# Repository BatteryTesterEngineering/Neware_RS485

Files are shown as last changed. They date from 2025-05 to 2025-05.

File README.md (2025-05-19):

# Neware BTS4000 RS-485 Protocol
This work is the reverse engineering of the Neware BTS4000 series battery cyclers RS-485 communication protocol.

## Division of Responsibilities
The Middle Machine is responsible for control and intepretation of the vast majority of the battery testing process, while the battery cyclers exclusively respond to commands from the middle machine.

For example, the termination conditions for test steps are evaluated and handled by the middle machine. The cyclers report current and voltage values as ADC readings, which the middle machine then converts to physical values. The testers themselves do run the active feedback control to maintain specified physical conditions: current, power, voltage, etc.

| Middle Machine   | Tester         | 
| --------- | ------------- | 
| Evaluates step termination conditions | Active feedback control to maintain step conditions (IE constant current, constant power, etc.) |
| Converts ADC values to physical values |  Sets channel LED status based on channel activity       | 
| Sets the data aquisition frequency    | Continuously Samples the ADCs  |

## RS-485 Bus
The Neware BTS4000 battery cycler system uses a full-duplex, 3 Mbps RS-485 physical bus to connect the middle machine to all of the test units.

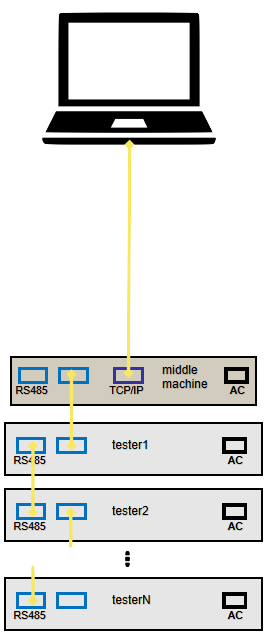
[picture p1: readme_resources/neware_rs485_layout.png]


RS-485 layout from [Neware's official guide](https://newarebattery.com/how-to-start-to-use-neware-bst4000-series/)

### Bus UART Settings

| Setting   | Value         | 
| --------- | ------------- | 
| Baud Rate | 3,000,000 bps | 
| Byte Size | 8 bits        | 
| Parity    | None          | 
| Stop Bits | 1             | 

### Full-Duplex
The RS-485 implementation by Neware is ***full-duplex***. Note that this is relatively unusual for RS-485 implementations. That means that the controller (middle machine) transmits messages on one channel (twisted copper pair), and the receivers (testers) transmit on another channel. 

> Side note: This could have been implemented as a half-duplex bus. This full-duplex communication is not technically needed, as the middle machine must send a request before any tester responds and the testers only respond after the middle machine requests. However, if the two channels are bridged, the communications fail between the middle machine and the testers. So, I guess, full-duplex it is.

### Pinout
The Neware BTS4000 middle machine and testers use RJ45 jacks and standard ethernet cables for RS-485 communications. Each machine has two ports which are wired in electrical parallel to allow for easy daisy chaining. There is no difference between the two ports.

The pinout is as follows:

| Middle Machine Function  | Tester Function | Ethernet Wire Color (T568B) | RJ45 Pin |
| ------ | ------ | ------------ | - |
| R- (B) | T- (Z) | Green        | 6 |
| R+ (A) | T+ (Y) | Green/White  | 3 |
| T- (Z) | R- (B) | Orange       | 2 |
| T+ (Y) | R+ (A) | Orange/White | 1 |
| GND    | GND    | Brown        | 8 |
| GND    | GND    | Brown/White  | 7 |

> RJ45 pins 4 and 5 (Ethernet T568B colors Blue and Blue/White) are unused.

## Neware Communication Protocol
The protocol appears to be a custom implementation on top of RS-485 and does not follow common standards such as Modbus RTU, Profibus, DMX512, BACnet MS/TP, etc.

### Overview
The middle machine begins all communications. Every response from the testers is a direct response to a request from the middle machine. The testers have a watchdog timeout such that they will turn off all charge or discharge activity on all channels if they do not hear a message from the middle machine every few seconds.

Every message is 36 bytes long and consists of one byte of machine addressing, one byte of channel addressing, one byte of message type ID, a one byte CRC, and 32 bytes of payload.

| byte 0 | byte 1 | byte 2 | byte 3 | bytes 4 - 35 |
| ------ | ------ | ------ | ------ | ------------ |
| Machine ID | Channel ID | Message Type ID | CRC | Message Type Dependent Payload

> Note: There is no time information provided by the testers. All timestamps are added upon message reception by the middle machine.

### Machine Addressing
Machine ID is 0 indexed, while it is presented to the user as 1 indexed. IE Machine ID 0 corresponds to the tester with ID 1.

### Channel Addressing
Channel ID is 0 indexed, while it is presented to the user as 1 indexed. IE Channel ID 7 corresponds to the tester Channel 8.

### Message Type ID
The message type ID byte defines what the message type is. Specifically, bit 0 is flag for request ('0' if the message is a request/comes from the middle machine) or response ('1' if the message is a response/comes from a tester), and the remaining seven bits define the message type.

| bit 0 | bits 1-7 |
| ----- | -------- |
| Request (0) / Response (1) Flag | Message Type |

Some known message type IDs are defined below:

| ID | Description |
| ----- | -------- |
| 0x00  | Tester Response (Ping) Request |
| 0x80  | Tester Presence (Ping) Acknowledge |
| 0x02  | Change Unit ID Request |
| 0x82  | Change Unit ID Acknowledge |
| 0x17  | Constant Voltage Charge Request |
| 0x97  | Constant Voltage Charge Acknowledge |
| 0x18  | Constant Voltage Discharge Request |
| 0x98  | Constant Voltage Discharge Acknowledge |
| 0x1A  | Constant Current Charge Request |
| 0x9A  | Constant Current Charge Acknowledge |
| 0x1B  | Constant Current Discharge Request |
| 0x9B  | Constant Current Discharge Acknowledge |
| 0x1C  | Constant Power Discharge Request |
| 0x9C  | Constant Power Discharge Acknowledge |
| 0x1F  | Voltage and Current Request |
| 0x9F  | Voltage and Current Acknowledge |
| 0x25  | End of Test Request |
| 0xA5  | End of Test Acknowledge |
| 0x31  | Constant Power Charge Request |
| 0xB1  | Constant Power Charge Acknowledge |

### CRC
The CRC byte is a crc8-maxim-dow calculated on a modified message. Since the CRC byte is in the middle of the message instead of at the end, the process of using it is a bit unusual. The CRC is calculated on the full 36 byte message, with a dummy 0x00 value subbed into byte 3. The calculated CRC is then swapped into byte 3 before the message is transmitted.

**Transmission CRC Calculation**:
1. Build the message as intended, leave a dummy '0x00' value in byte 3.
2. Calculate the CRC using a crc8-maxim-dow algorithm on the 36 byte message with the dummy byte.
3. Place the calculated CRC in byte 3.
4. Transmit the 36 byte message.

**Reception CRC Checking**:
1. Receive the 36 byte message.
2. Copy the CRC out of byte 3.
3. Replace byte 3 with '0x00'
4. Calculate the CRC using a crc8-maxim-dow algorithm on the 36 byte message with the dummy byte
5. Compare the calculated CRC with the stored CRC from the message, checking for equality

-- Or --

4. Append the copied CRC byte to the end of the message
5. Calculate the CRC using a crc8-maxim-dow algorithm on the now 37 byte array (message + appended CRC)
6. Check the calculated CRC for equality with '0x00'

### Payload
The payload is message type dependent. Some known payloads are described below.

**Message 0x17: Constant Voltage Charge Request**

| Name | Byte Position | Physical Value to Bus Value Mapping |
| ----- | -------- | ----- |
| Voltage  | Bytes 4-7 | Physical Value = Bus Value / 3225.6 |

**Message 0x97: Constant Voltage Charge Acknowledge**

There is no payload for a Constant Voltage Charge Acknowledge

**Message 0x1A: Constant Current Charge Request**

| Name | Byte Position | Physical Value to Bus Value Mapping |
| ----- | -------- | ----- |
| Current  | Bytes 4-7 | Physical Value = Bus Value / Current Range Divisor |
| Current Range  | Byte 8 | See Table in 0x9F: Voltage and Current Acknowledge |

**Message 0x9A: Constant Current Charge Acknowledge**

There is no payload for a Constant Current Charge Acknowledge

**Message 0x1B: Constant Current Discharge Request**

| Name | Byte Position | Physical Value to Bus Value Mapping |
| ----- | -------- | ----- |
| Current  | Bytes 4-7 | Physical Value = Bus Value / Current Range Divisor |
| Current Range  | Byte 8 | See Table in 0x9F: Voltage and Current Acknowledge |

**Message 0x9B: Constant Current Discharge Acknowledge**

There is no payload for a Constant Current Discharge Acknowledge

**Message 0x1C: Constant Power Discharge Request**

| Name | Byte Position | Physical Value to Bus Value Mapping |
| ----- | -------- | ----- |
| Power  | Bytes 4-7 | Physical Value = Bus Value / Power Range Divisor |
| Power Range  | Byte 12 | See Table |

Strangely, only power range of 0x02 has ever been seen in logs, when setting the power value from 0.5W to 60W

| Power Range | Name | Description | Power Range Divisor |
| ----- | -------- | ----- | -------- |
| 0x00  | Low Range | ? A | ? |
| 0x01  | Mid Range | ? A | ? |
| 0x02  | High Range | 0 - 60 W | 268.8 |

**Message 0x9C: Constant Power Discharge Acknowledge**

There is no payload for a Constant Power Discharge Acknowledge

**Message 0x1F: Voltage and Current Request**

There is no payload for a Voltage and Current Request

**Message 0x9F: Voltage and Current Acknowledge**

| Name | Byte Position | Physical Value to Bus Value Mapping |
| ----- | -------- | ----- |
| Voltage  | Bytes 4-7 | Physical Value = Bus Value / 3225.6 |
| Current  | Bytes 8-11 | Physical Value = Bus Value / Current Range Divisor |
| Current Range  | Byte 33 | See Table |
| Channel Status | Byte 35 | See Table |

| Current Range | Name | Description | Current Range Divisor |
| ----- | -------- | ----- | -------- |
| 0x00  | Low Range | 0 - 1 A | 16128 |
| 0x01  | Mid Range | 1 - 6 A | 2688 |
| 0x02  | High Range | 6 - 12 A | 1344 |

| Channel Status | Description |
| ----- | ----- |
| 0x00  | Channel Active |
| 0x01  | Channel Invalid/Error |
| 0x02  | Channel Rest |

**Message 0x25: End of Test Request**

There is no payload for an End of Test Request

**Message 0xA5: End of Test Acknowledge**

There is no payload for an End of Test Acknowledge

**Message 0x31: Constant Power Charge Request**

| Name | Byte Position | Physical Value to Bus Value Mapping |
| ----- | -------- | ----- |
| Power  | Bytes 4-7 | Physical Value = Bus Value / Power Range Divisor |
| Power Range  | Byte 12 | See Table |

Strangely, only power range of 0x02 has ever been seen in logs, when setting the power value from 0.5W to 60W

| Power Range | Name | Description | Power Range Divisor |
| ----- | -------- | ----- | -------- |
| 0x00  | Low Range | ? A | ? |
| 0x01  | Mid Range | ? A | ? |
| 0x02  | High Range | 0 - 60 W | 268.8 |

**Message 0xB1: Constant Power Charge Acknowledge**

There is no payload for a Constant Power Charge Acknowledge

***TODO! Add more***

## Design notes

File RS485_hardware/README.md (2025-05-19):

# Neware BTS4000 RS485 USB Interface

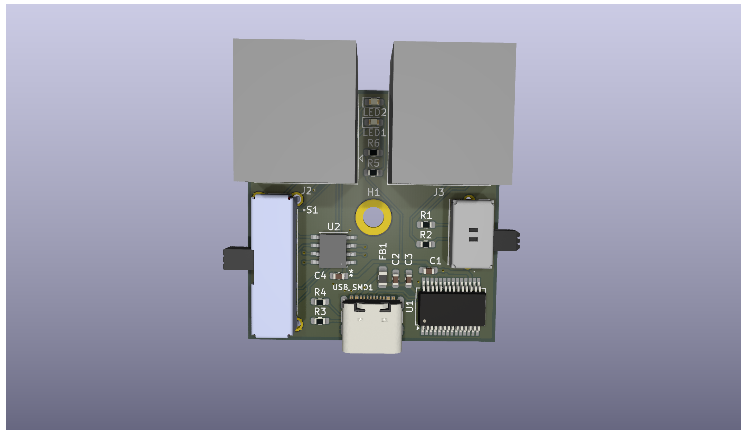
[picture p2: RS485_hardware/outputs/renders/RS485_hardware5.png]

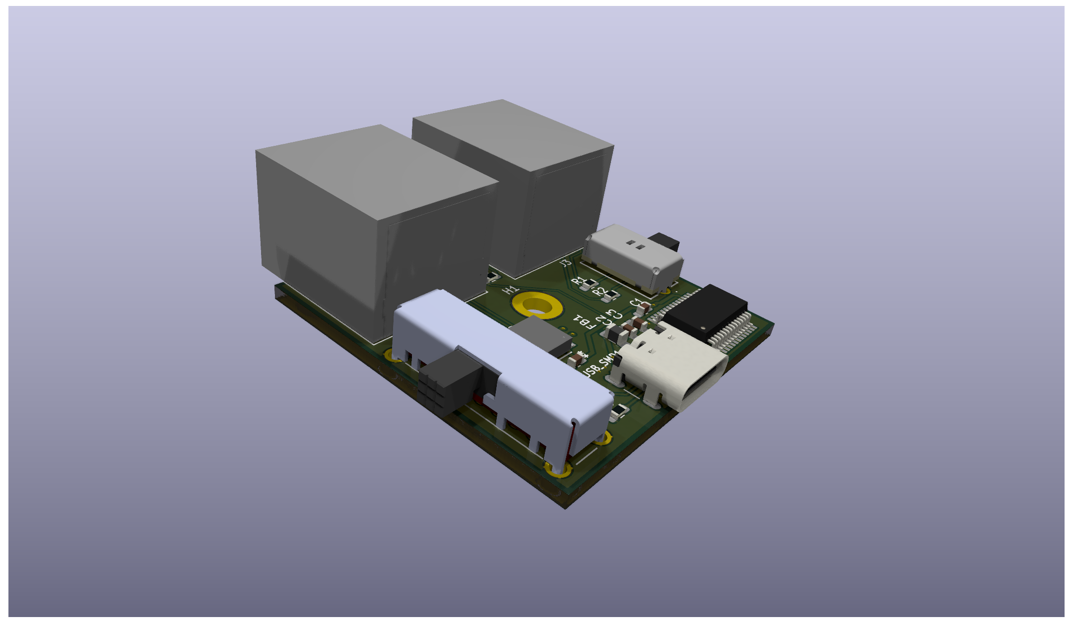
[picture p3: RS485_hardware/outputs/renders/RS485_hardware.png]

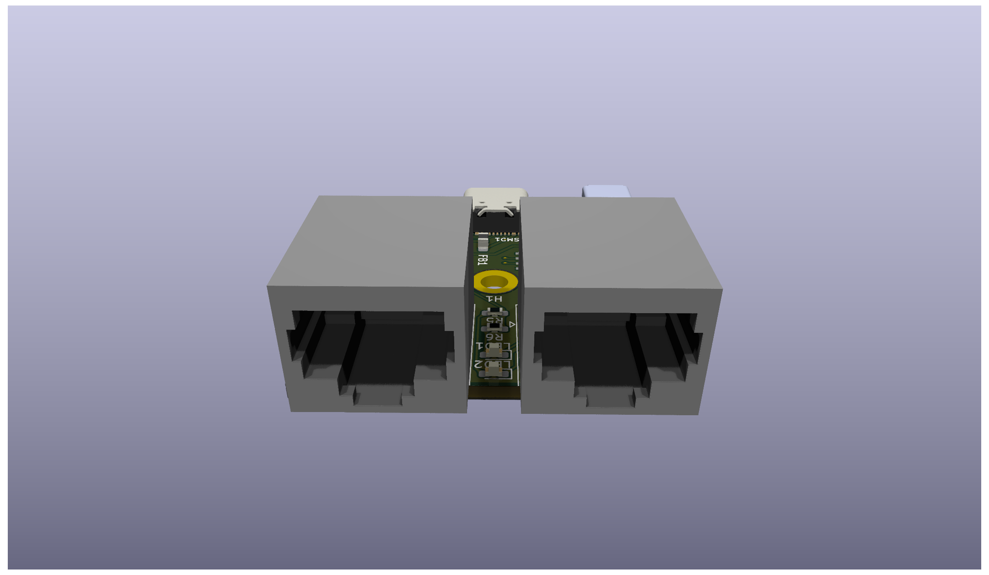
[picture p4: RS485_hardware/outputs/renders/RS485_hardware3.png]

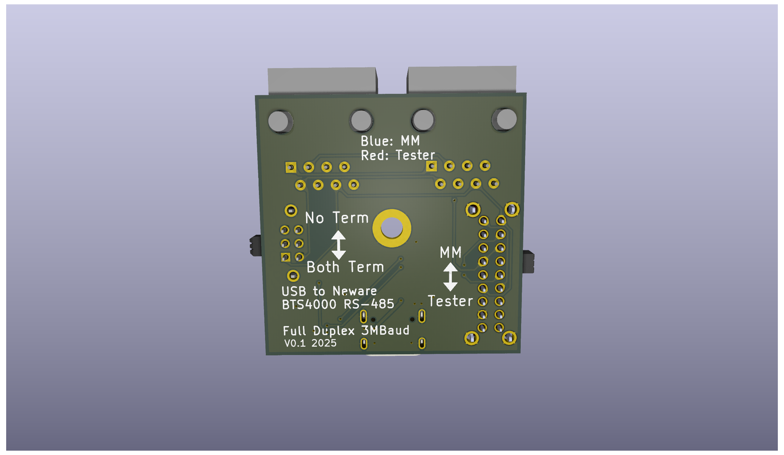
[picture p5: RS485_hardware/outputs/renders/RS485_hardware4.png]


This is the Kicad project and output files for a USB Adapter that allows any computer to listen and transmit on the Neware BTS4000 RS485 bus. The adapter is based on the FTDI FT232RN chip, which includes drivers for all major operating systems. The transciever is a MaxLinear SP3077E, which allows for full duplex 3MBaud communication.

## RS485 Bus Connectors
The bus connectors are intended to duplicate the RS485 bus connections on a Middle Machine or Battery Tester. There are 2 RJ45 Jacks which are wired in parallel, allowing the device to be used in the same daisy-chain fashion as a Neware device. 

## Switches
The adapter includes 2 slide switches.

### Switch 1
Toggles the adapter between "Middle Machine Mode" and "Tester Mode". Since the RS485 bus is a full duplex bus, it matters which line the adapter is receiving on, and which it is transmitting on. With the switch slid towards the RJ45 jacks, the adapter acts as a middle machine, receiving on the same line that battery testers are transmitting on, and transmitting on the line that battery testers are receiving on. With the switch slid towards the USB-C jack, the adapter acts as tester, receiving from the middle machine and transmitting to the middle machine.

| Switch Position | Adapter Mode | Adapter TX | Adapter RX | LED Color |
| ------ | ------ | ------ | ------ | ------ |
| Towards RJ45 | Middle Machine | Middle Machine TX | Middle Machine RX | Blue |
| Towards USB-C | Tester | Middle Machine RX | Middle Machine TX | Red |

### Switch 2
Toggles the RS485 Termination Resistors on or off. With the switch slid towards the RJ45 jacks, there are no termination resistors on the bus. With the switch slid towards the USB-C jack, the adapter terminates the TX and RX busses with a 120Ω resistor on each bus. Whether or not you need the termination resistors enabled dependes on the length of the bus and what other devices are on the bus. A typical RS485 bus has a temination resistor enabled on both physical ends of the bus.

## PC Connection
The connection to a computer is a USB-C connector configured to run at USB 2.0 speeds. The USB connector has 5.1kΩ resistors on the CC lines, which allow it to work with USB C<->C cables or USB A<->C cables.

# Manufacturing
The ```outputs/manufacturing_files``` subfolder contains gerber and OBD files needed for PCB manufacturing, as well as the BOM file. The BOM contains manufacturer and part number data for digikey and LCSC to make sourcing parts easy regardless of where the boards are manufactured.

## Hand Assembly
All passives are 0603 or larger, with the large-pad footprints chosen to allow for hand soldering. Similarly, the pitch of all components should be large enough for hand soldering.

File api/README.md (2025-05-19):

# API
This is the only folder that you need to deploy in order to use the Neware RS485 Python API.

## Top Level Directory
In the top level directory are all the things that you need to interact with to emulate a middle machine (implemented) or a battery tester (todo: coming soon).

- ```middle_machine.py```: This file allows you to emulate the behavior of a middle machine. It includes functions to request and receive voltage and current from a battery cycler, as well as command test steps.

- ```example_battery_controls.py```: This file is an example showing you how to use ```middle_machine.py``` to run a series of basic test steps on a battery cell and record the results.

## RS485 Sub-directory

> ***Everything in this directory is autogenerated!***

This directory is entirely autogenerated from ```generate_neware_rs485_api_files.py``` in the ```bus_definition``` top-level directory and should not need to be updated manually.

This directory contains ```rs485_api.py``` which is the top level file for creating/packing and matching/unpacking an arbitrary message. This is what ```middle_machine.py``` interfaces with in order to creates and receives messages. It is extremely unlikely that you will need to interface with this file directly, and you should instead use ```middle_machine.py``` or one of the other machine emulator files to build your applications.

### Messages Sub-Sub-directory

> ***Everything in this directory is autogenerated!***

This directory is entirely autogenerated from ```generate_neware_rs485_api_files.py``` in the ```bus_definition``` top-level directory and should not need to be updated manually.

This directory contains one file per message, each of which contains one class with two functions for packing and unpacking the message payload respectively.

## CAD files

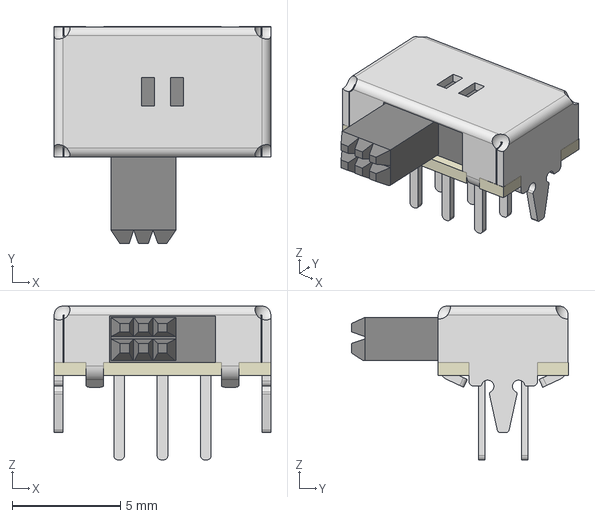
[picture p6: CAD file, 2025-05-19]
RS485_hardware/components/EG2211/EG2211.stp
10.0 x 10.0 x 7.10 mm

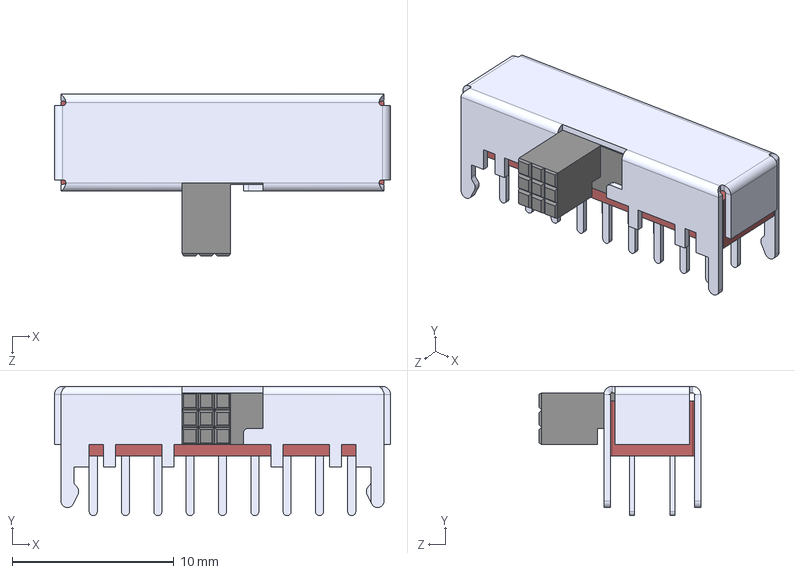
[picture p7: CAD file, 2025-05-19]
RS485_hardware/components/EG6201/EG6201.step
20.8 x 8.00 x 10.0 mm

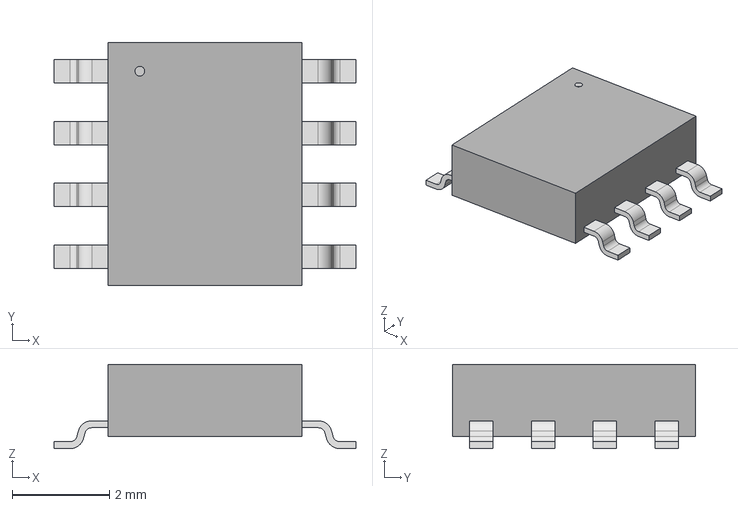
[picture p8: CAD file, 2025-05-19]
RS485_hardware/components/SP3077EEN_L/SOIC8_3P99X4P98.step
6.20 x 4.98 x 1.73 mm

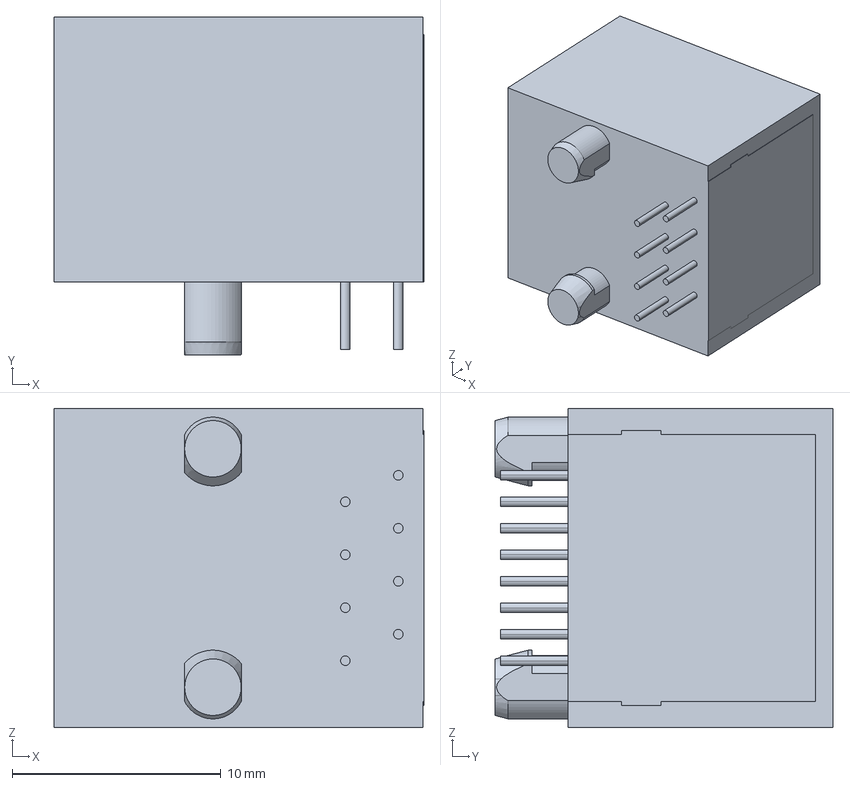
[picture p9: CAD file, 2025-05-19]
RS485_hardware/components/54602-908LF/54602-908LFc.stp
17.7 x 16.2 x 15.3 mm

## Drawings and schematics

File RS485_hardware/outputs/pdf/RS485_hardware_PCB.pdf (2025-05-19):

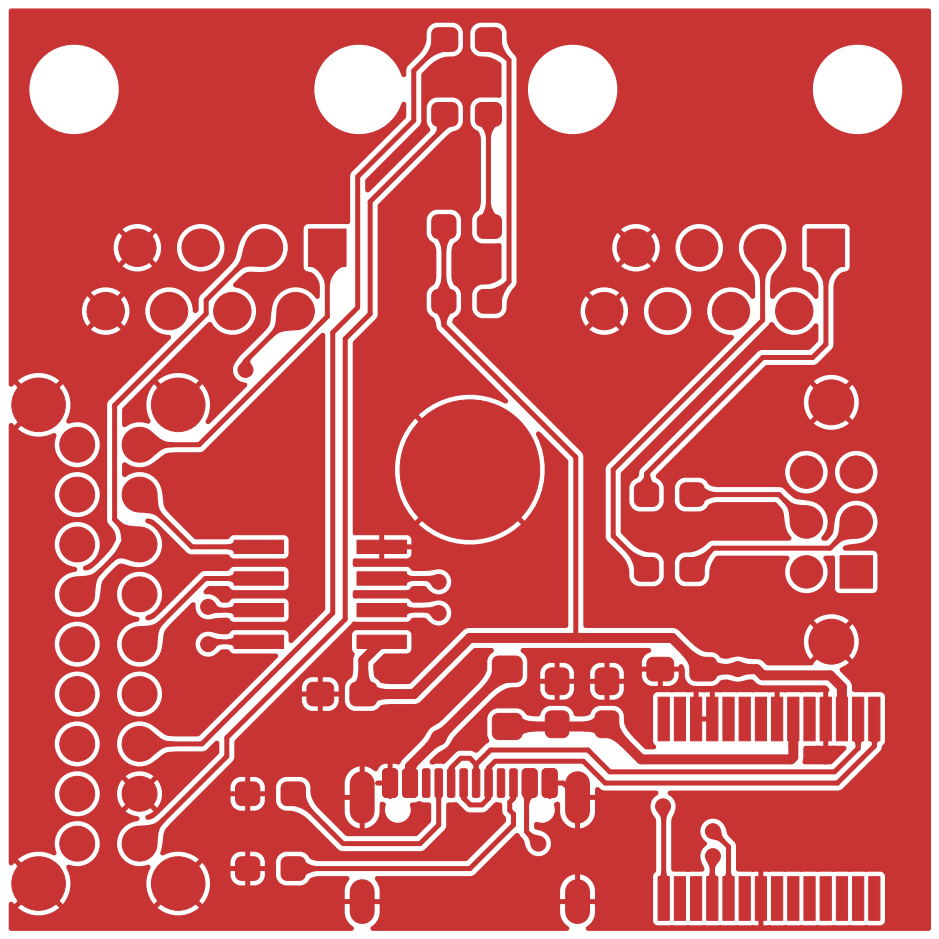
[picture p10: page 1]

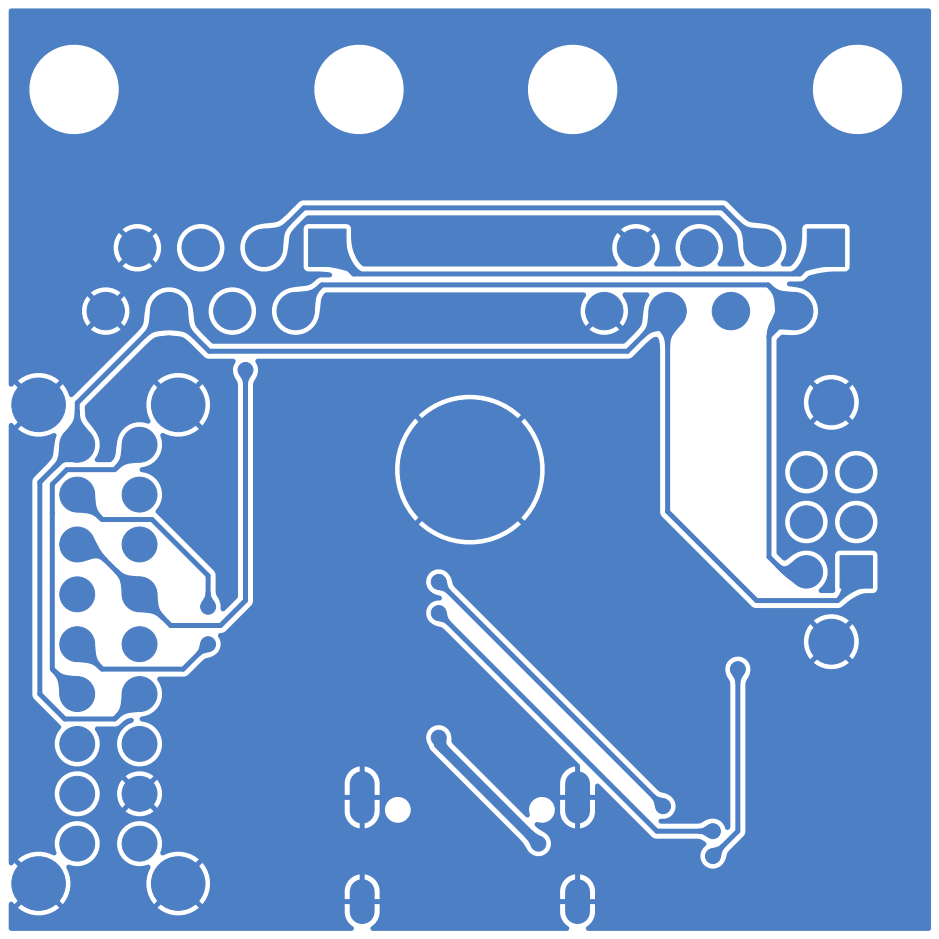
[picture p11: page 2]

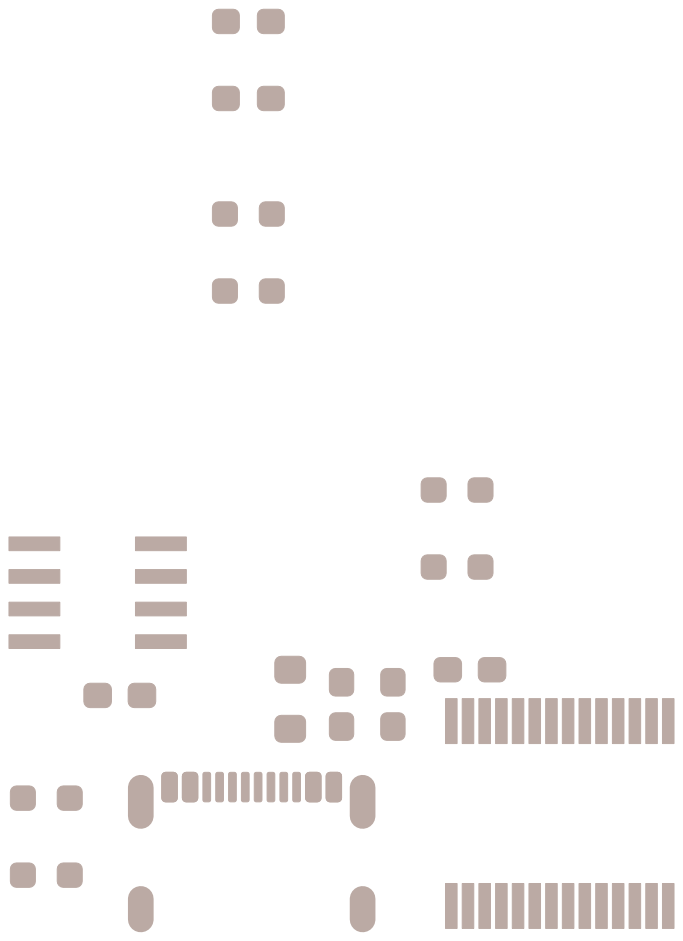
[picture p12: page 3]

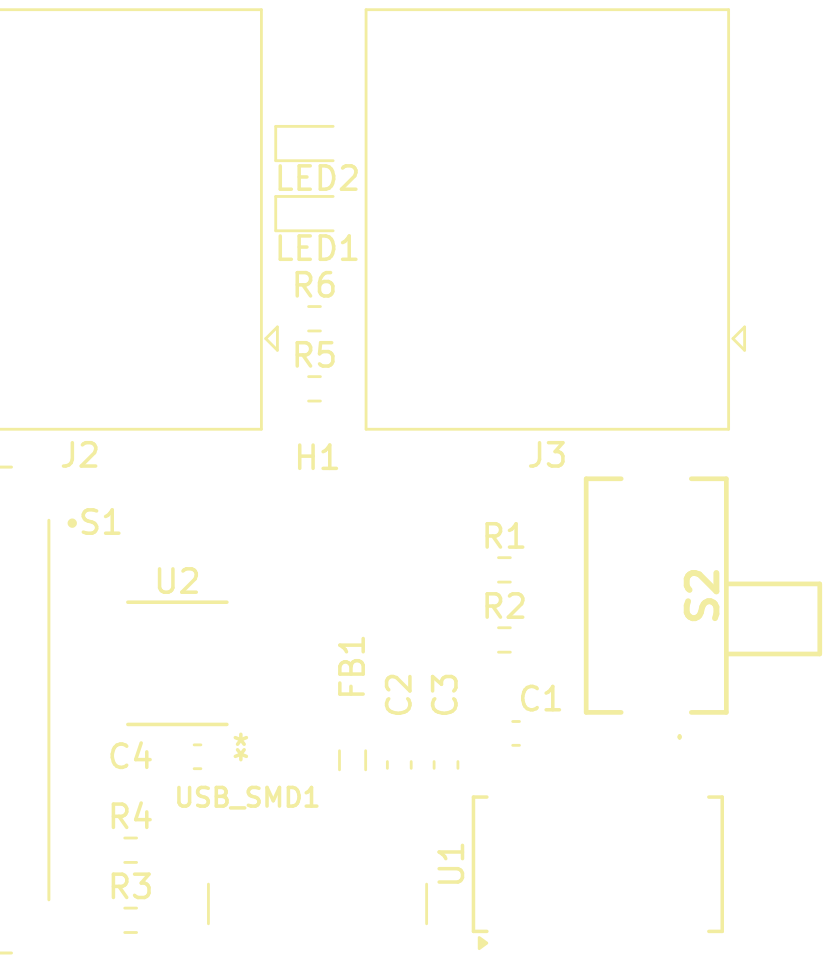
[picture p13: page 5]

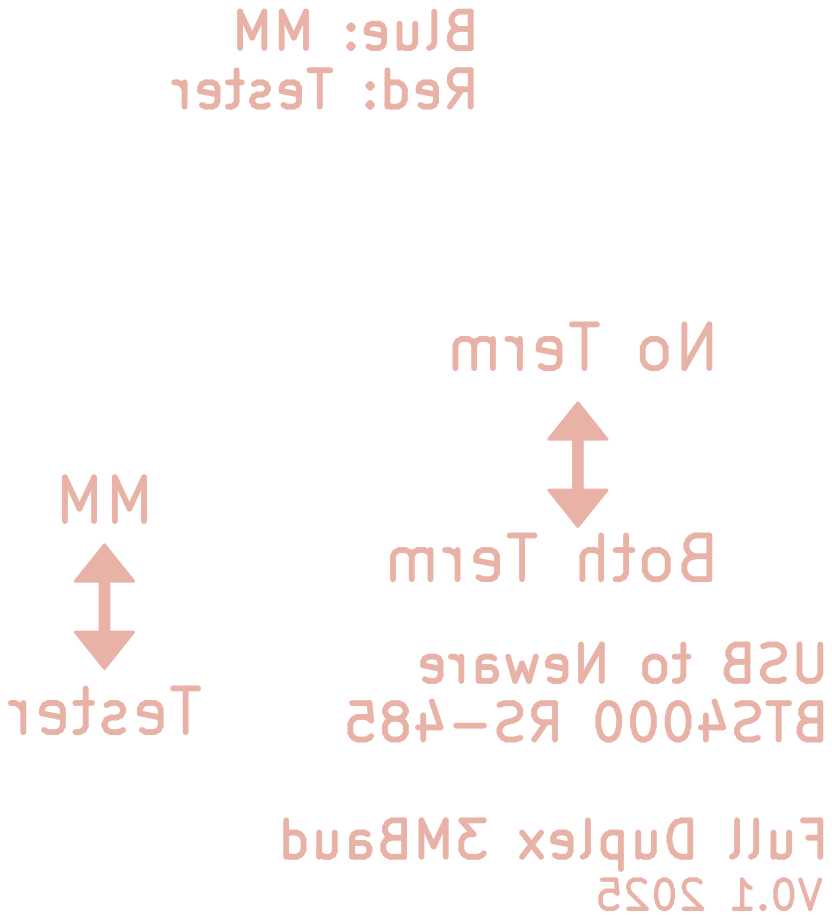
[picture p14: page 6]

Term Both MM Blue: Tester Red:

3MBaud Duplex Full Term No

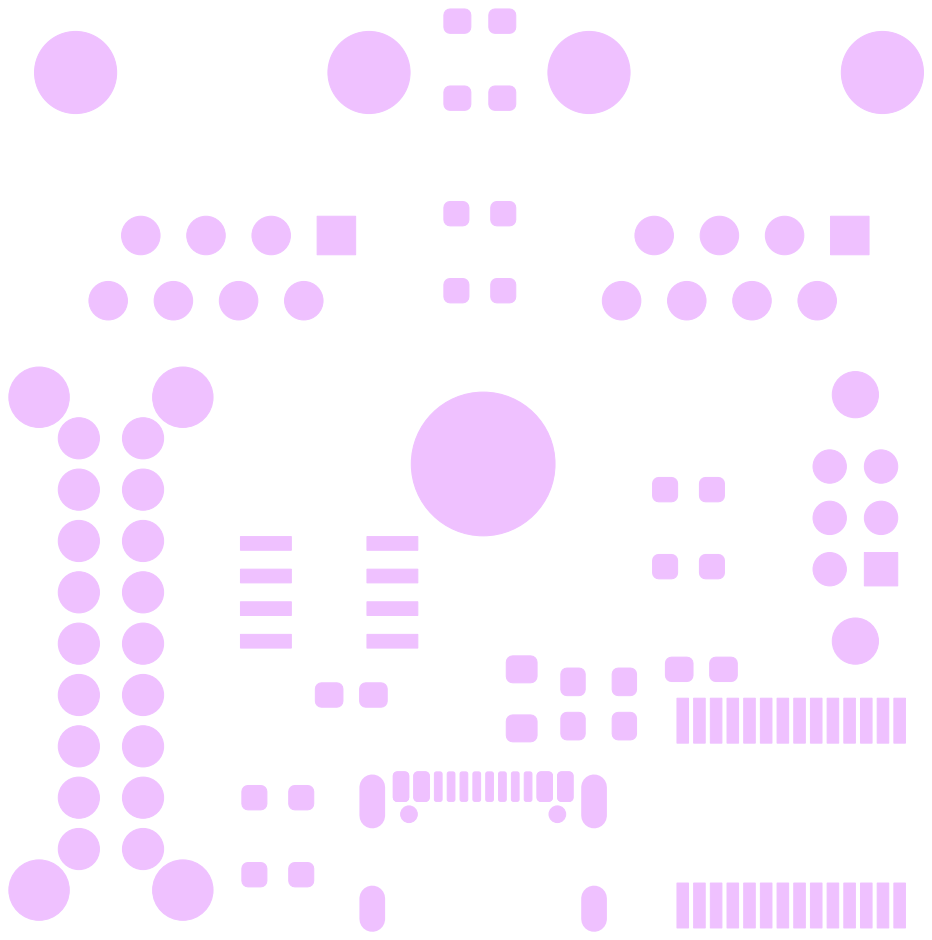
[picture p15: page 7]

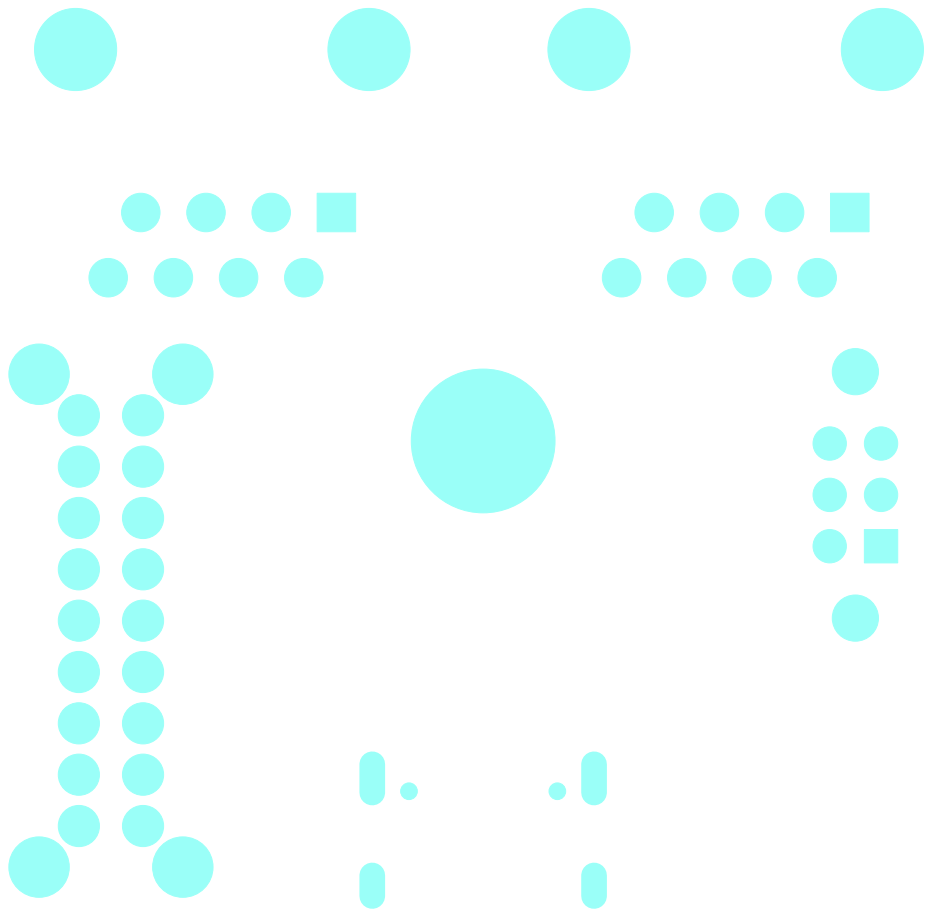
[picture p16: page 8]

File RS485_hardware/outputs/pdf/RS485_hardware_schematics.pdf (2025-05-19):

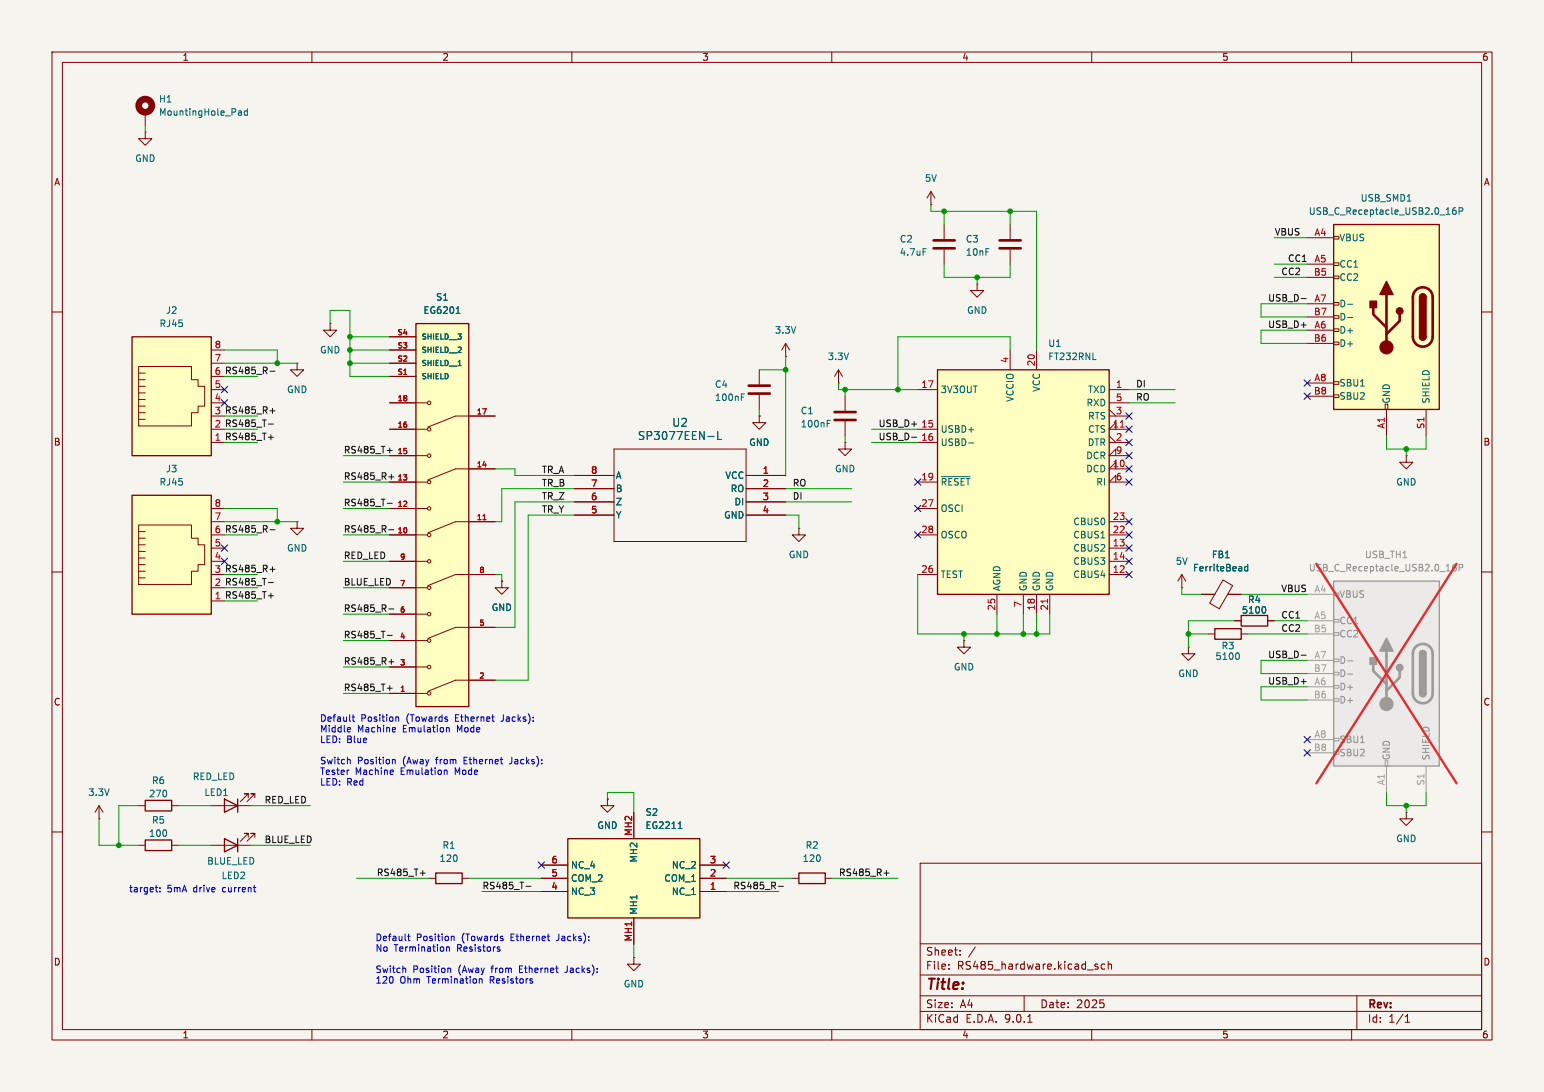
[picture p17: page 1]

7 VCC 20 GND 18 GND 21 TXD 1 RXD 5 RTS 3 CTS 11 DTR 2 DCR 9 DCD 10 RI 6 CBUS0 23 CBUS1 22 CBUS2 13 CBUS3 14 CBUS4 12 U1 FT232RNL GND SHIELD S1 GND A1 VBUS A4 CC1 A5 CC2 B5 D- A7 D- B7 D+ A6 D+ B6 SBU1 A8 SBU2 B8 USB_TH1 USB_C_Receptacle_USB2.0_16P C1

Id: 1/1 Title: File: RS485_hardware.kicad_sch Sheet: / GND

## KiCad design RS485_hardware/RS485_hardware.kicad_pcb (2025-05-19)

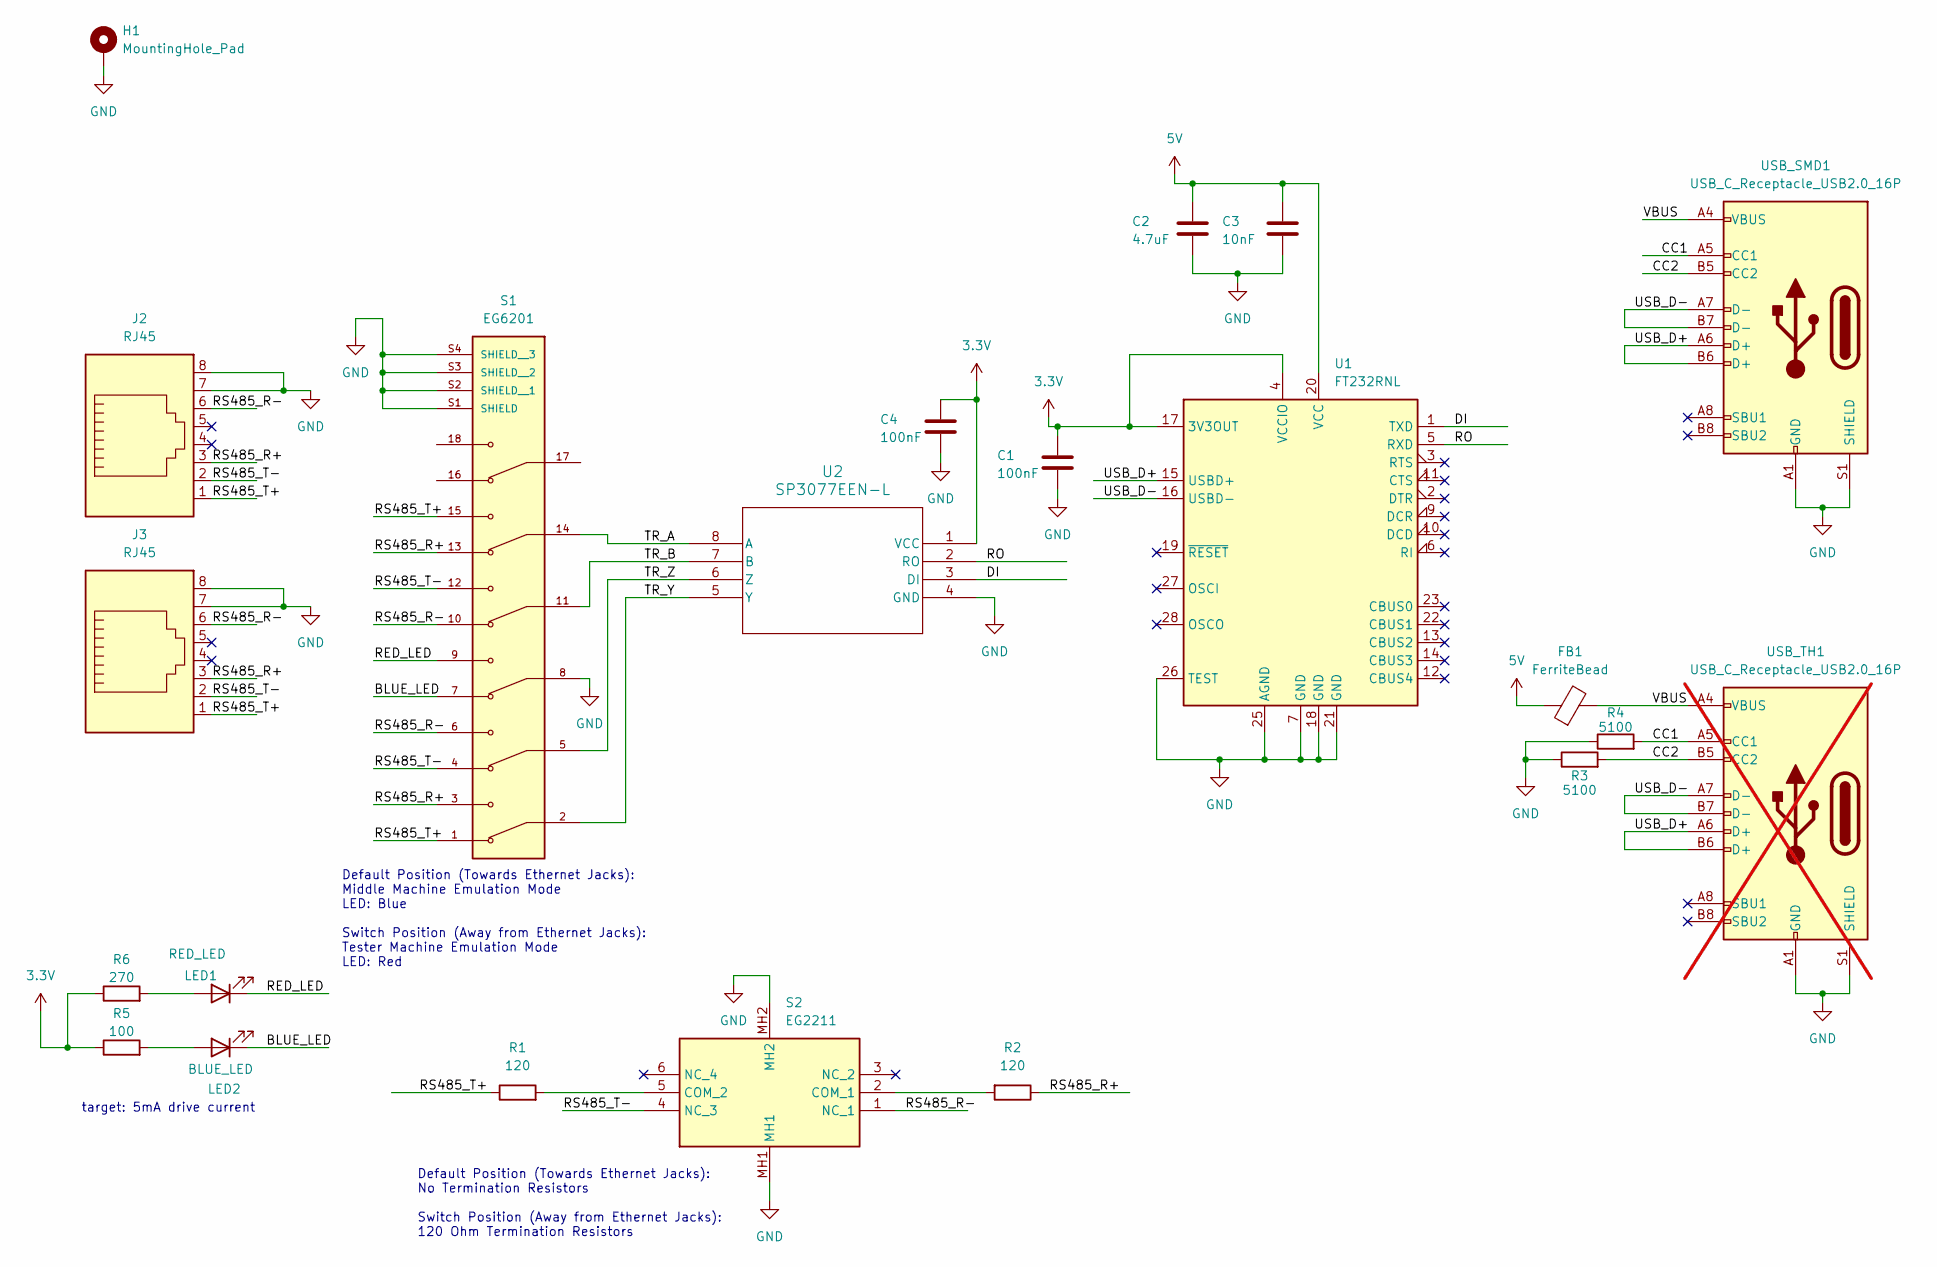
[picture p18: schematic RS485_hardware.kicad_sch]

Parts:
C1, C4: 100nF; C_0603_1608Metric_Pad1.08x0.95mm_HandSolder
C2: 4.7uF; C_0603_1608Metric_Pad1.08x0.95mm_HandSolder
C3: 10nF; C_0603_1608Metric_Pad1.08x0.95mm_HandSolder
FB1: FerriteBead; L_0805_2012Metric_Pad1.05x1.20mm_HandSolder
H1: MountingHole_Pad; MountingHole_3.2mm_M3_DIN965_Pad
J2, J3: RJ45; RJ45_Amphenol_54602-x08_Horizontal
LED1: RED_LED; LED_0603_1608Metric_Pad1.05x0.95mm_HandSolder
LED2: BLUE_LED; LED_0603_1608Metric_Pad1.05x0.95mm_HandSolder
R1, R2: 120; R_0603_1608Metric_Pad0.98x0.95mm_HandSolder
R3, R4: 5100; R_0603_1608Metric_Pad0.98x0.95mm_HandSolder
R5: 100; R_0603_1608Metric_Pad0.98x0.95mm_HandSolder
R6: 270; R_0603_1608Metric_Pad0.98x0.95mm_HandSolder
S1: EG6201; SW_EG6201; PARTREV B
S2: EG2211; Mouser Part Number 612-EG2211
U1: FT232RNL; SSOP-28_5.3x10.2mm_P0.65mm
U2: SP3077EEN-L; SOIC8_3P99X4P98
USB_SMD1: USB_C_Receptacle_USB2.0_16P; USB_C_Receptacle_GCT_USB4105-xx-A_16P_TopMnt_Horizontal
USB_TH1: USB_C_Receptacle_USB2.0_16P; USB_C_Receptacle_GCT_USB4085; not fitted

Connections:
3.3V: C1.1, C4.1, R5.1, R6.1, U1.4 (VCCIO), U1.17 (3V3OUT), U2.1 (VCC)
5V: C2.1, C3.1, FB1.1, U1.20 (VCC)
/BLUE_LED: LED2.1 (K), S1.7
/CC1: R4.2, USB_SMD1.A5 (CC1), USB_TH1.A5 (CC1)
/CC2: R3.2, USB_SMD1.B5 (CC2), USB_TH1.B5 (CC2)
/DI: U1.1 (TXD), U2.3 (DI)
/RED_LED: LED1.1 (K), S1.9
/RO: U1.5 (RXD), U2.2 (RO)
/RS485_R+: J2.3, J3.3, R2.1, S1.3, S1.13
/RS485_R-: J2.6, J3.6, S1.6, S1.10, S2.1 (NC_1)
/RS485_T+: J2.1, J3.1, R1.1, S1.1, S1.15
/RS485_T-: J2.2, J3.2, S1.4, S1.12, S2.4 (NC_3)
/TR_A: S1.14, U2.8 (A)
/TR_B: S1.11, U2.7 (B)
/TR_Y: S1.2, U2.5 (Y)
/TR_Z: S1.5, U2.6 (Z)
/USB_D+: U1.15 (USBD+), USB_SMD1.A6 (D+), USB_SMD1.B6 (D+), USB_TH1.A6 (D+), USB_TH1.B6 (D+)
/USB_D-: U1.16 (USBD-), USB_SMD1.A7 (D-), USB_SMD1.B7 (D-), USB_TH1.A7 (D-), USB_TH1.B7 (D-)
/VBUS: FB1.2, USB_SMD1.A4 (VBUS), USB_SMD1.A9 (VBUS), USB_SMD1.B4 (VBUS), USB_SMD1.B9 (VBUS), USB_TH1.A4 (VBUS), USB_TH1.A9 (VBUS), USB_TH1.B4 (VBUS), USB_TH1.B9 (VBUS)
GND: C1.2, C2.2, C3.2, C4.2, H1.1, J2.7, J2.8, J3.7, J3.8, R3.1, R4.1, S1.8, S1.S1 (SHIELD), S1.S2 (SHIELD__1), S1.S3 (SHIELD__2), S1.S4 (SHIELD__3), S2.MH1, S2.MH2, U1.7 (GND), U1.18 (GND), U1.21 (GND), U1.25 (AGND), U1.26 (TEST), U2.4 (GND), USB_SMD1.A1 (GND), USB_SMD1.A12 (GND), USB_SMD1.B1 (GND), USB_SMD1.B12 (GND), USB_SMD1.S1 (SHIELD), USB_TH1.A1 (GND), USB_TH1.A12 (GND), USB_TH1.B1 (GND), USB_TH1.B12 (GND), USB_TH1.S1 (SHIELD)
unnamed: LED1.2 (A), R6.2
unnamed: LED2.2 (A), R5.2
unnamed: R2.2, S2.2 (COM_1)
unnamed: R1.2, S2.5 (COM_2)

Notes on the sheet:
Default Position (Towards Ethernet Jacks): Middle Machine Emulation Mode LED: Blue Switch Position (Away from Ethernet Jacks): Tester Machine Emulation Mode LED: Red
target: 5mA drive current
Default Position (Towards Ethernet Jacks): No Termination Resistors Switch Position (Away from Ethernet Jacks): 120 Ohm Termination Resistors

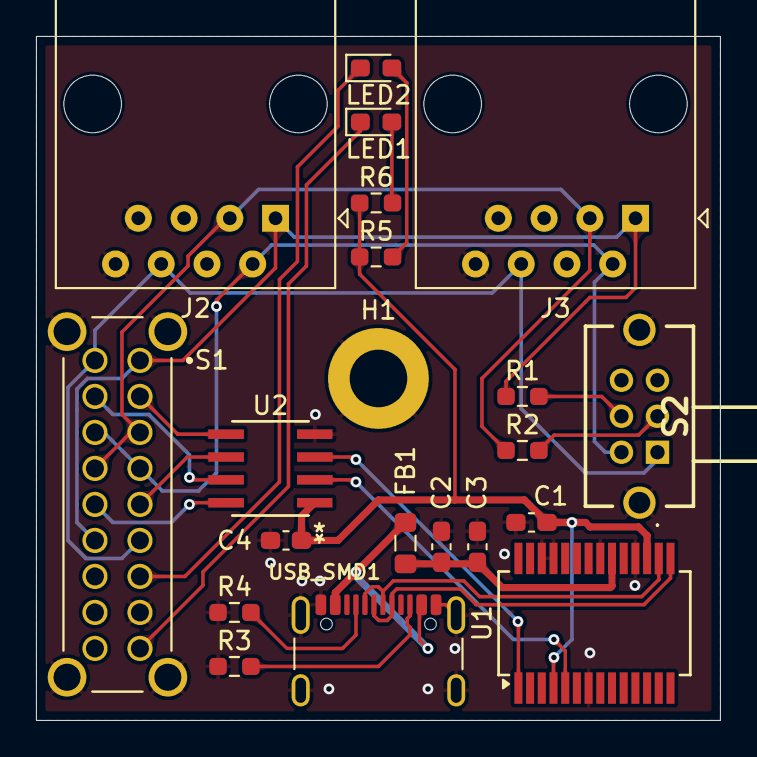
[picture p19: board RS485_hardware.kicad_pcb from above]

Board: 2 copper layers, 38.0 x 38.0 mm, 21 parts (0 on the bottom side), 24 nets.
